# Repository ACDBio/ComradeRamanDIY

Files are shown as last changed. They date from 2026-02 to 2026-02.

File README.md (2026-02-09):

# ComradeRamanDIY
A DIY 3D printed Raman system with a CCD spectrometer using based on 90° scattering geometry and 100mW 780 nm laser. Adjustment-free
This repository documents the physical Raman system: overview, .stl and FreeCad files for 3d printing, bill of materials, and examples of the acquired spectra.

### Free software which can be used for calibration, data acquisition, processing, visualization, and search in the reference databases is available [here](https://github.com/ACDBio/raman-open-forge-imai).

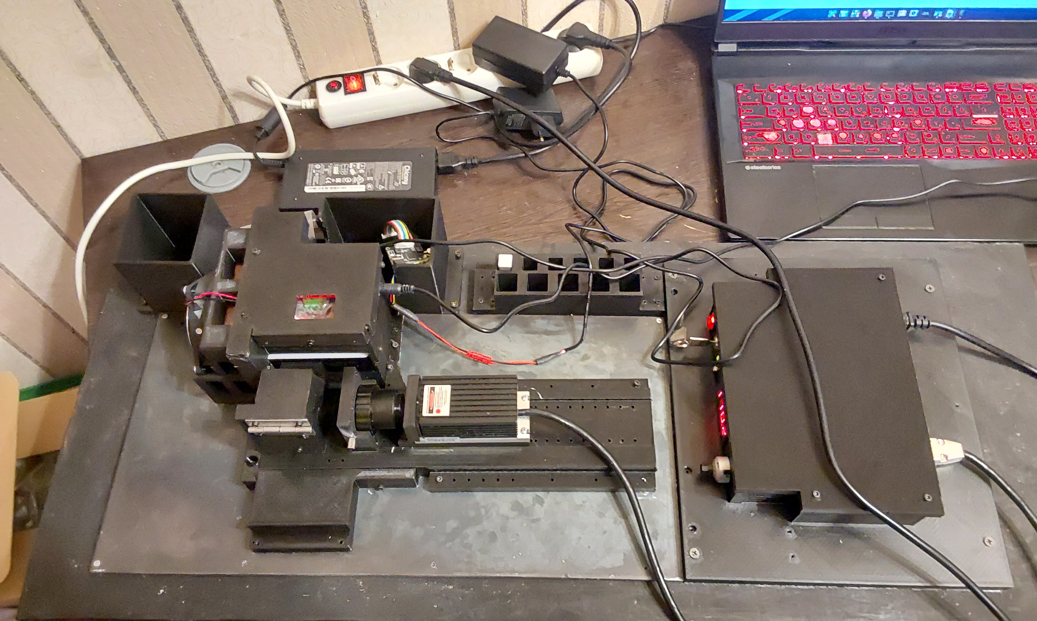
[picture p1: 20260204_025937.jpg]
SystemView


---

## About the system

ComradeRamanDIY is a Raman setup built from commercially available components and custom 3D-printed mechanics.

Key design choices:

- 90° collection geometry   
- external TEC cooling of the CCD spectrometer  
- stack of budget filters for effective filtration of the laser line

The system was designed for stable measurement of liquid samples in cuvettes.
---

## Current system performance
Comparison of the DMSO spectra obtained with the system and the mprofessional probe after Raman shift [software](https://github.com/ACDBio/raman-open-forge-imai) calibration. Note: the DIY system spectra are normalized by top peak. No preprocessing was used. Smoothing was set to 1/10 in both cases.
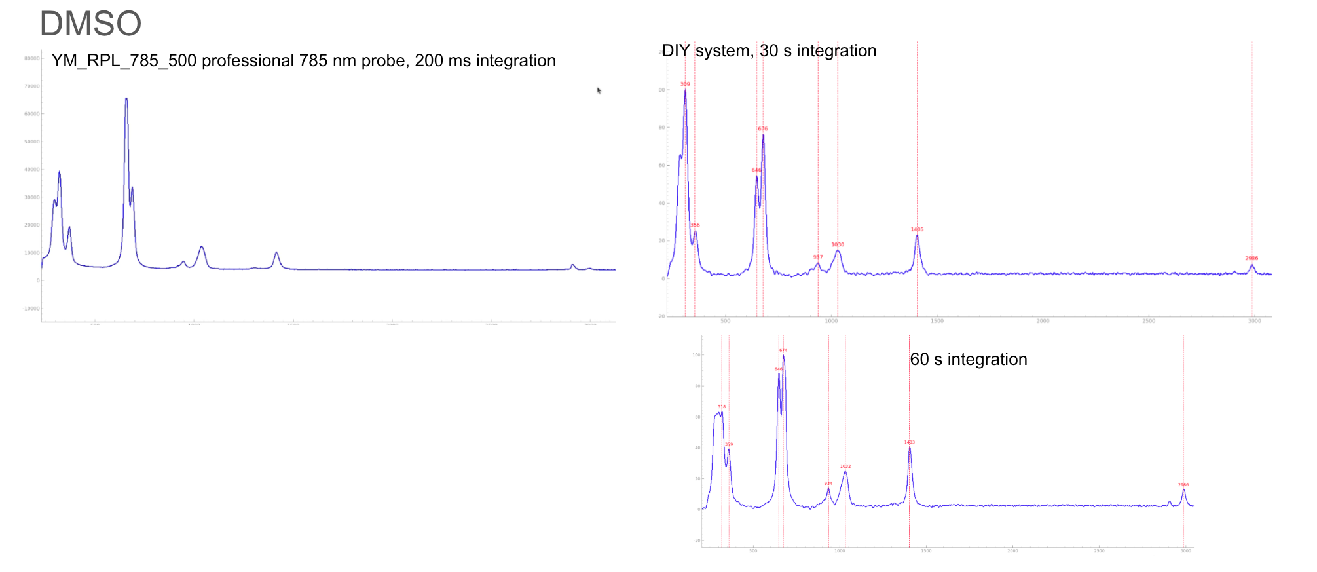
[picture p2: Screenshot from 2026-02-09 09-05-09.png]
DMSO spectra comparison


After system calibration with [YM_RPL_785_500](https://aliexpress.ru/item/1005010193725685.html?spm=a2g2w.orderdetail.0.0.20384aa6LKfzBg&sku_id=12000051478540187&_ga=2.6013747.1429933141.1770309479-1631170546.1742897773), DIY spectra peak positions match the reference database spectra (from ramanbase.org) without re-calibration.
E.g. for isopropyl alcohol:
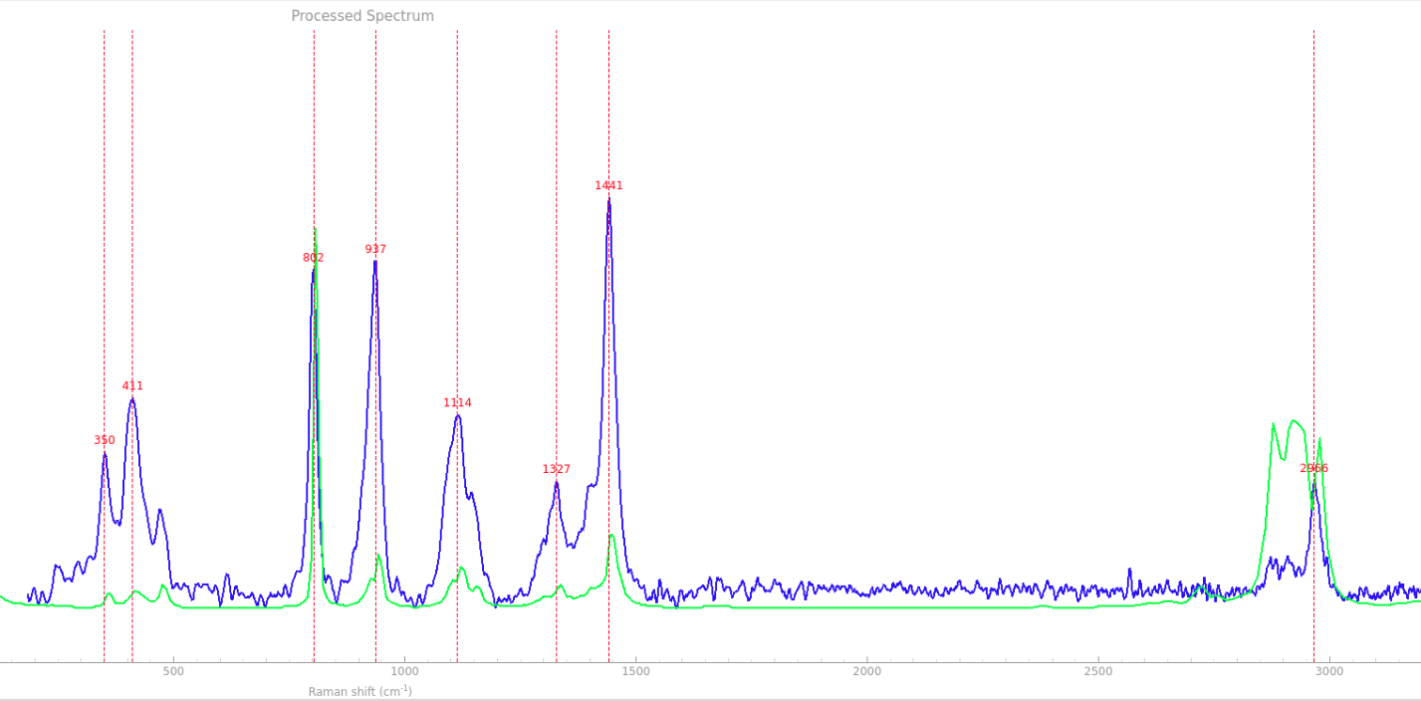
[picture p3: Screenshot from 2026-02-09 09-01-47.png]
Isopropyl alcohol


---

## Implementation Notes
The system is sensitive to vertical shift of the cuvette holder before assembly. We attached an .stl bottom plates which can be tested and glued to the bottom before assembly if it is off.
In the final system the counts for DMSO at 30 s integration should be at least ~17-20k without significant noise at ~15 degrees if it is assembled correctly.
It is recommended to cool with the TEC system implemented here to 15 degrees - it allows larger integration times up to 60 s.
The focusing distance of the SZMCTV 1/2 Microscope Camera Adapter is adjustable and should be moved to the extreme position for optimal performance.

## BILL OF MATERIALS
Total cost (with a new CCD spectromter): ~1800 USD
1. PETG 3d printing filament for printing the .stl
2. 800 nm long-pass filters 4-14 pieces (the current system uses 14 pieces but the quality of spectra don't change substantially from 4 pieces). We used 5.9x5.9 mm IR camera filters from [this shop](https://aliexpress.ru/store/911601353?spm=a2g2w.orderdetail.0.0.18794aa6WkrNWx&page=3) for ~ 2$. 1-2 filters from [here](https://aliexpress.ru/item/1005009606845139.html?spm=a2g2w.orderdetail.0.0.10bb4aa6kRWllm&sku_id=12000049611215568&_ga=2.133597321.606840197.1770619478-1631170546.1742897773) also work, but you will need to adjust the cuvette holder.
4. [NF780 Narrow Band filter](https://aliexpress.ru/item/1005008883212898.html?spm=a2g2w.orderdetail.0.0.d7e94aa6Bp8xzT&sku_id=12000047075793792&_ga=2.26257338.606840197.1770619478-1631170546.1742897773) for laser cleaning.
5. [15 degree IR LED PMMA lens](https://aliexpress.ru/item/32820431045.html?spm=a2g2w.orderdetail.0.0.75834aa6qalnJD&sku_id=64707315106&_ga=2.189769388.606840197.1770619478-1631170546.1742897773) for light collection (is inserted in the cuvette holder)
6. [Quartz cuvette](https://aliexpress.ru/item/32793982308.html?spm=a2g2w.orderdetail.0.0.2bdd4aa6R19moS&sku_id=63840647083&_ga=2.17671998.606840197.1770619478-1631170546.1742897773) 10 mm light path
7. [IRM785 CCD spectrometer](https://aliexpress.ru/item/1005009187077048.html?spm=a2g2w.orderdetail.0.0.671d4aa6tsgBNN&sku_id=12000048233983566&_ga=2.33651750.606840197.1770619478-1631170546.1742897773)
8. [SZMCTV 1/2 Microscope Camera Adapter](https://aliexpress.ru/item/32855848880.html?spm=a2g2w.favourites.0.0.778e4aa6S5wLJN&sku_id=10000001989770343) for laser focusing. Microscope objectives also work, but you will need to adjust focusing distance in the 3d model.
9. [TEC1-12715](https://aliexpress.ru/item/1005003070412441.html?shpMethod=CAINIAO_ECONOMY&sku_id=12000023786453944&spm=a2g2w.productlist.search_results.5.53b447bfnGnVcq) for CCD spectrometer cooling with the radiator (here - a 7х8 cm copper one was used) and a fan.
10. [780 nm 100mW DPSS laser](https://aliexpress.ru/item/1005009999890335.html?spm=a2g2w.orderdetail.0.0.74364aa6jLg0Pi&sku_id=12000050803608976&_ga=2.197611304.606840197.1770619478-1631170546.1742897773) Here - LaseVer was used.
11. Steel plate 6mm (optional)

# Acknowledgments
Special thanks to [Imai Optics](http://www.imaioptics.com/) for supporting the project by providing a discount on [YM_RPL_785_500](https://aliexpress.ru/item/1005010193725685.html?spm=a2g2w.orderdetail.0.0.20384aa6LKfzBg&sku_id=12000051478540187&_ga=2.6013747.1429933141.1770309479-1631170546.1742897773), which was instrumental in testing the setup during development.
Also thyanks to [ramanbase.org](https://ramanbase.org/) developers and contributors and ramanspy developers.

The cuvette holder provided here can also be used with [Imai Optics](http://www.imaioptics.com/) probe [YM_RPL_785_500](https://aliexpress.ru/item/1005010193725685.html?spm=a2g2w.orderdetail.0.0.20384aa6LKfzBg&sku_id=12000051478540187&_ga=2.6013747.1429933141.1770309479-1631170546.1742897773).

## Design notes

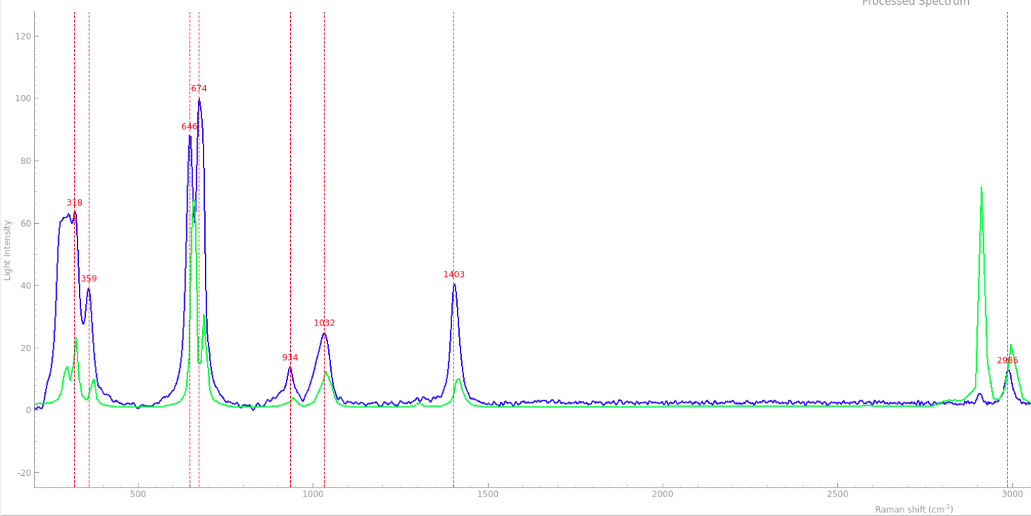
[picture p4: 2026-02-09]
Screenshot from 2026-02-09 09-02-16.png

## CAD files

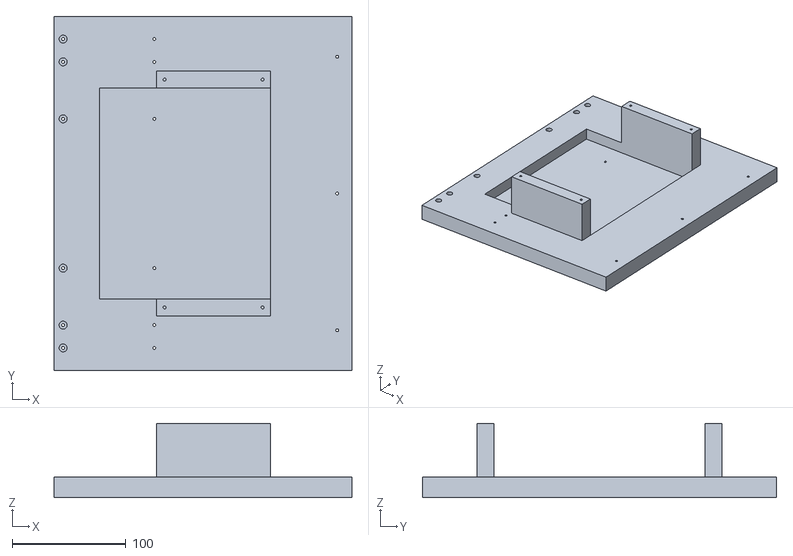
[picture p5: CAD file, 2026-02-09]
DPSS_driver_base.stl
261.5 x 311.0 x 65.0

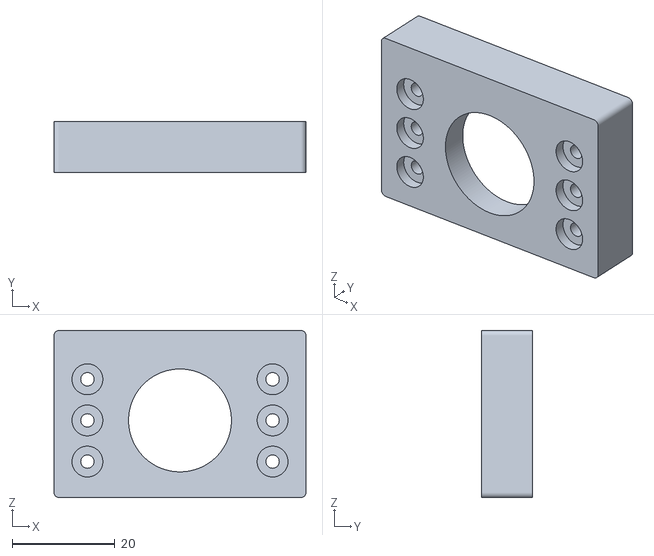
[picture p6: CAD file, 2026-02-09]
NarrowBandFilterCaseCoverExt.stl
49.0 x 10.0 x 32.5

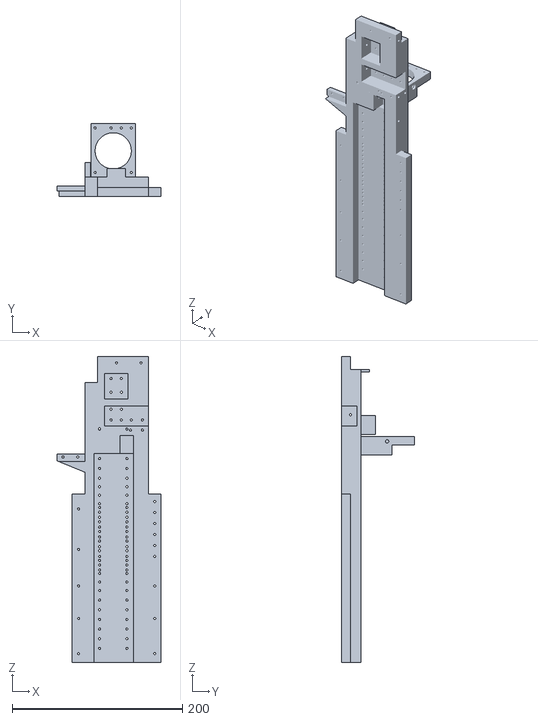
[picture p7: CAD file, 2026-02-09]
ExtExtBase.stl
122.5 x 85.5 x 359.5

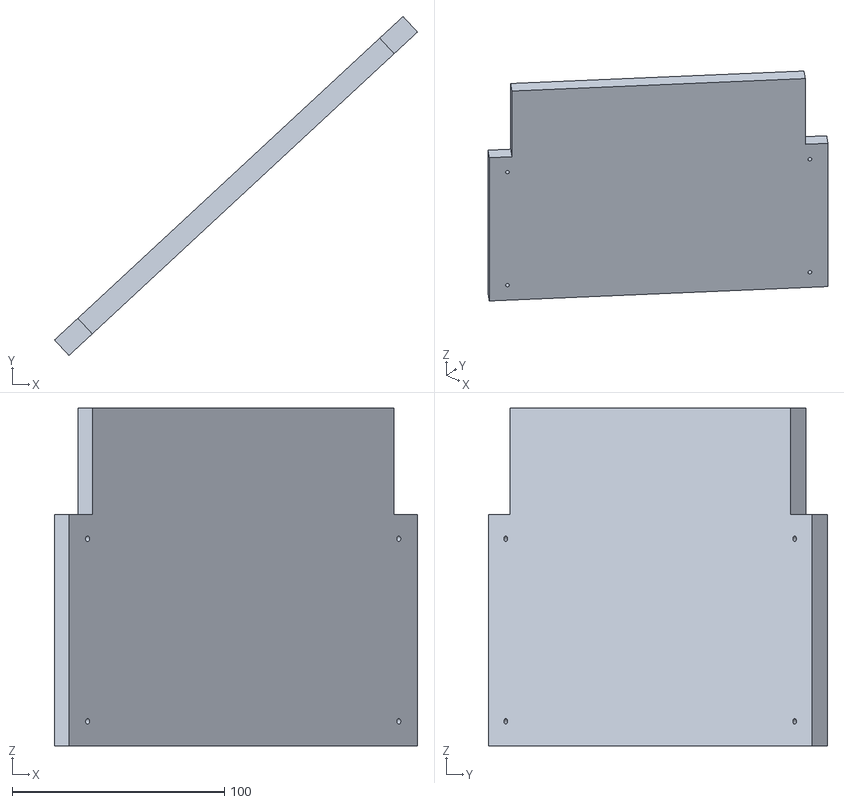
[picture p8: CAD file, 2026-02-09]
DPSS_driver_cap.stl
171.0 x 159.7 x 159.0

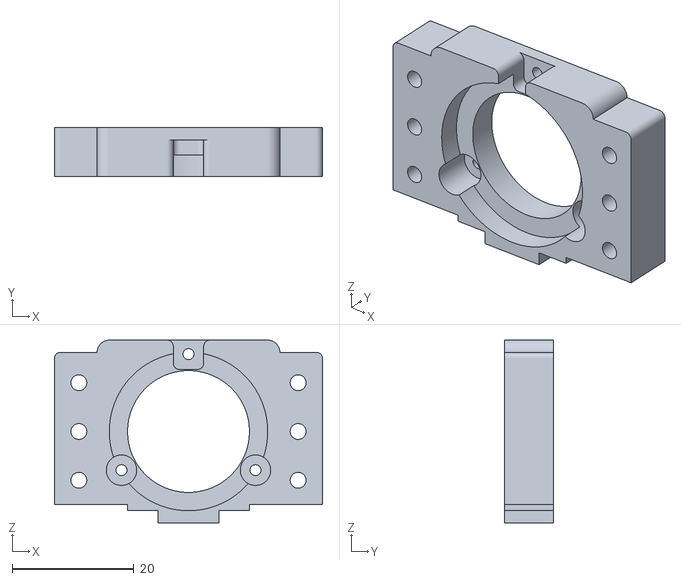
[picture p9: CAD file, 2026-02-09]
NarrowBandFilterCaseExt_thickened.stl
44.0 x 8.00 x 30.0

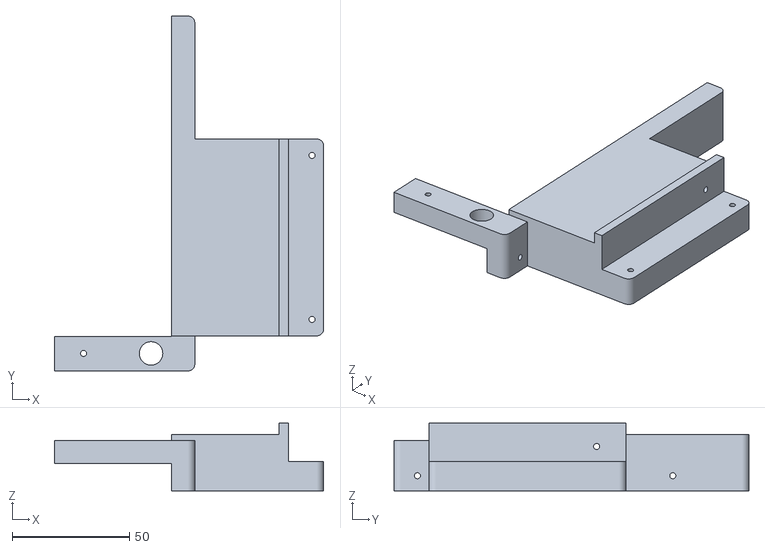
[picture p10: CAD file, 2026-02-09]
BaseExtension.stl
115.0 x 151.5 x 29.0

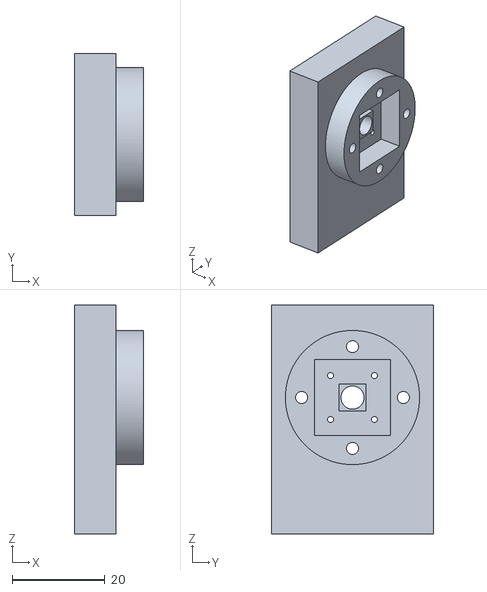
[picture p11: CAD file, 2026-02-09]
FreespaceCCDAdapter.stl
14.9 x 35.0 x 49.5

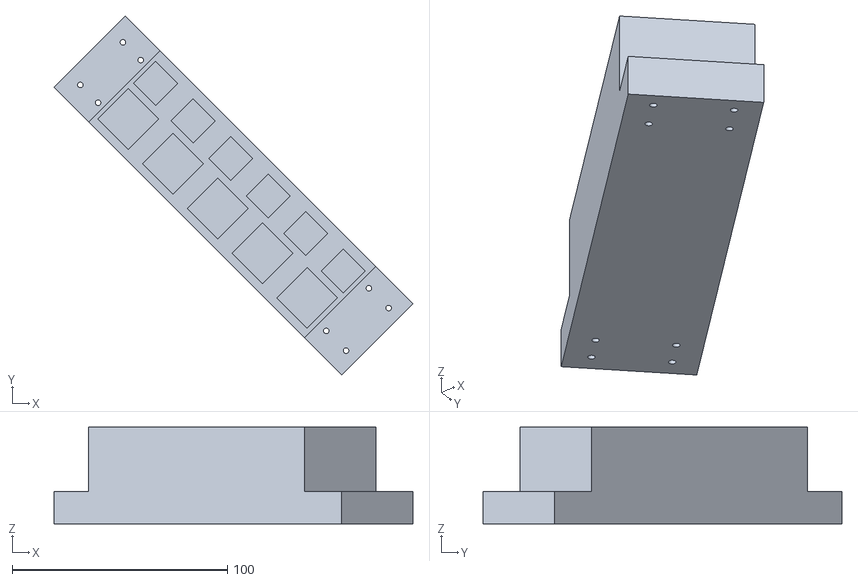
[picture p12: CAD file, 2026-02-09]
CuvetteStand.stl
166.9 x 166.9 x 45.0

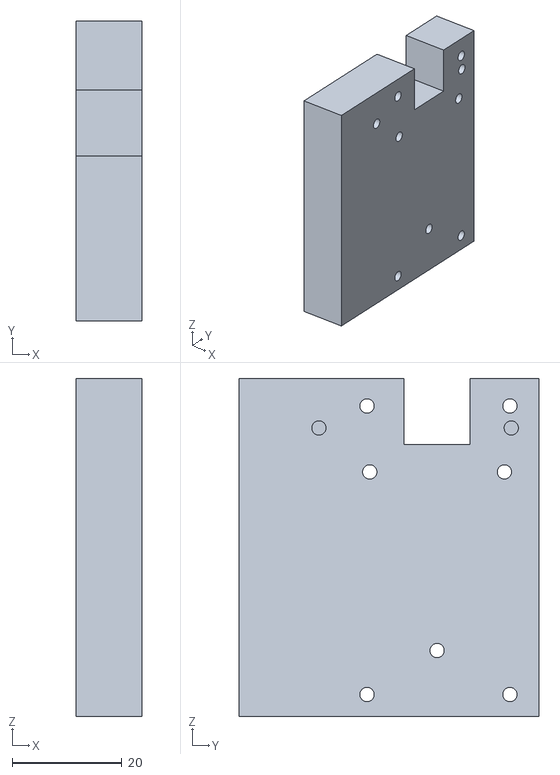
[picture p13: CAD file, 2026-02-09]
CuvholdbackShortened.stl
12.0 x 54.5 x 61.5

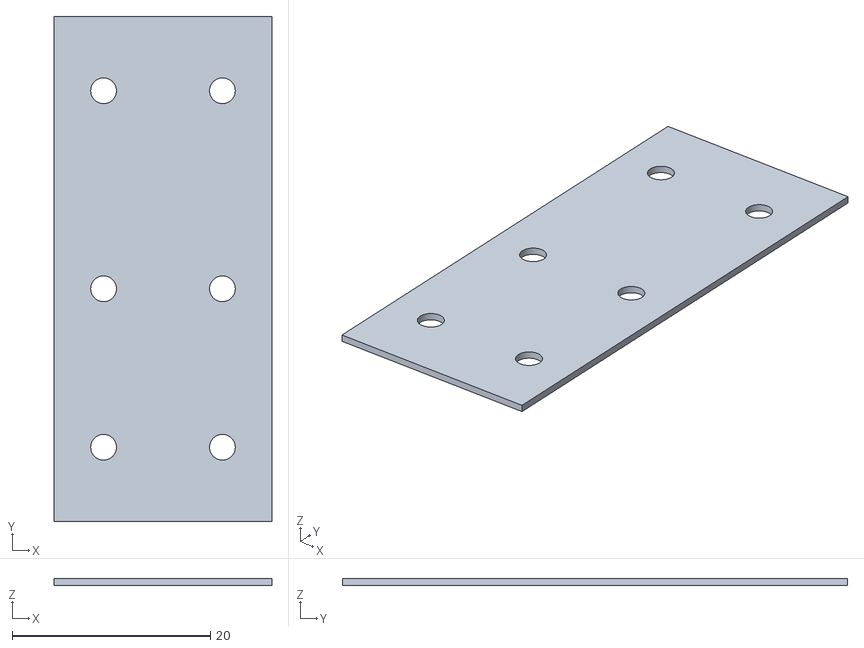
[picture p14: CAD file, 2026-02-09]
bottomext05mm.stl
22.0 x 51.0 x 0.7

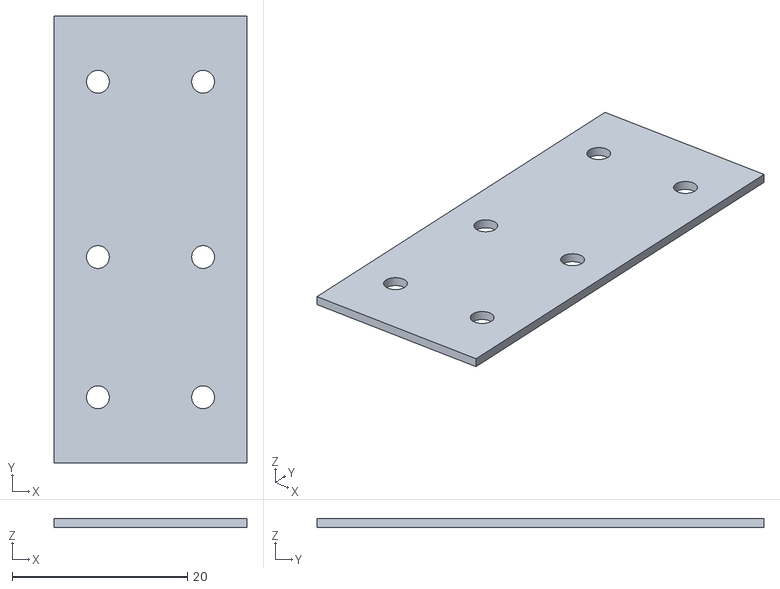
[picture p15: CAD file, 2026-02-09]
bottomext1mm.stl
22.0 x 51.0 x 1.00

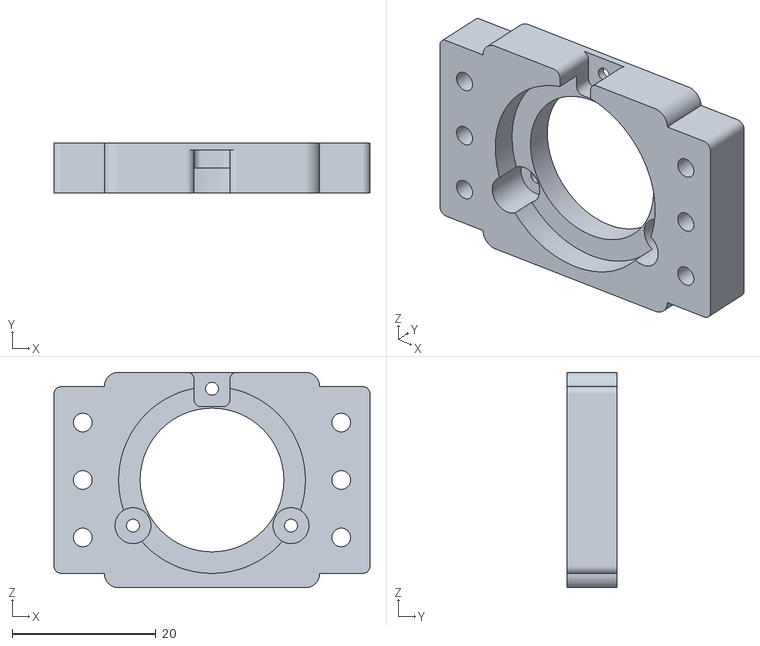
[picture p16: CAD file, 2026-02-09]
NarrowBandFilterCaseExt.stl
44.0 x 7.00 x 30.0

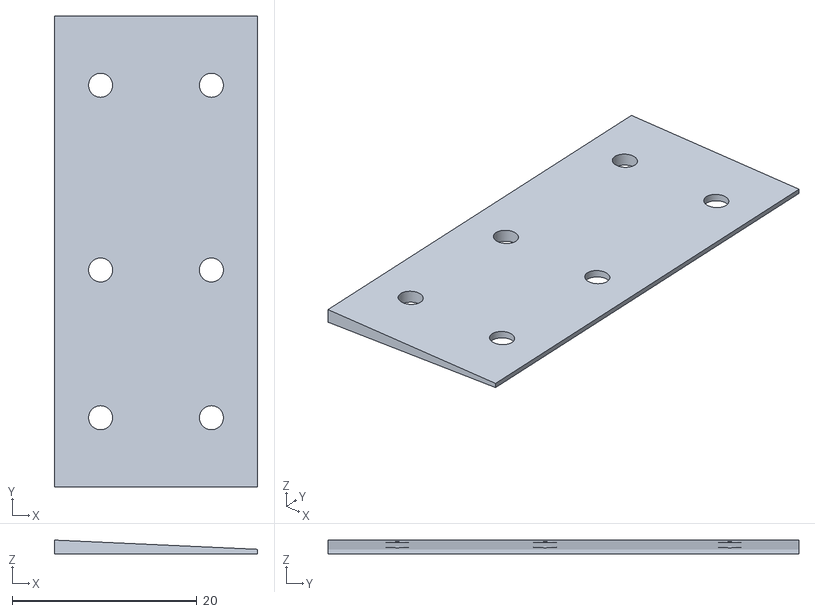
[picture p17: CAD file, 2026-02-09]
bottomext155mm.stl
22.0 x 51.0 x 1.50

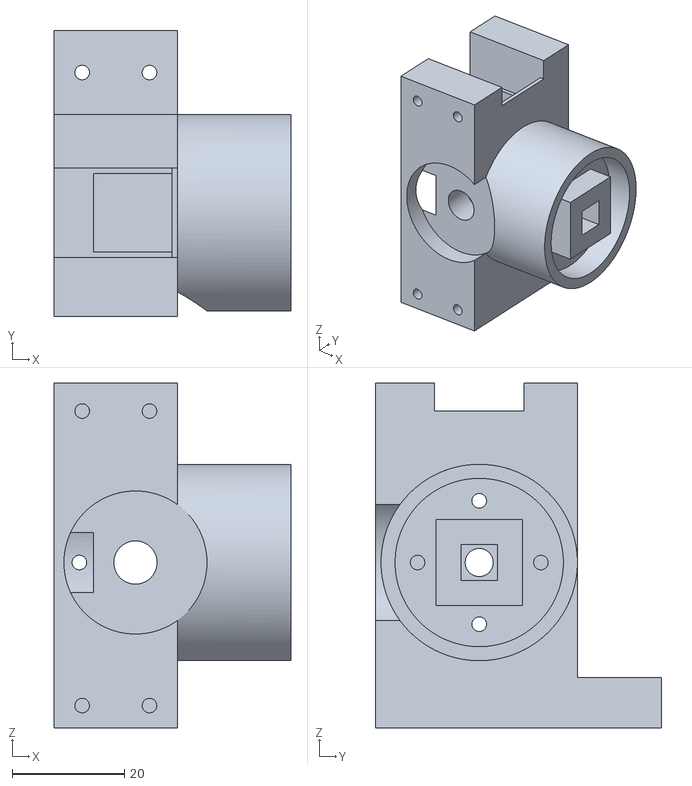
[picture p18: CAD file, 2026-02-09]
CuvholdShortened.stl
42.2 x 51.0 x 61.5

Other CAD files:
Boxsid.stl

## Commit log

2026-02-09 Update README with cuvette holder and performance details
    Added information about the cuvette holder compatibility and current system performance with DMSO spectra comparison.
2026-02-09 Add bill of materials to README
    Added a bill of materials section with detailed components and links.
